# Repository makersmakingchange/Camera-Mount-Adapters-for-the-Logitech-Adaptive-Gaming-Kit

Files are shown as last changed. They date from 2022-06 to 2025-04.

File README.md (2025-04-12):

# Camera Mount Adapters for the Logitech Adaptive Gaming Kit

This Documentation covers information for both the full kit (12 adapters) and for a single adapter for one button.

The Camera Mount Adapters for Logitech Adaptive Gaming Kit are inexpensive, easy, and quick to build adapters for the four different Buttons from the [Logitech Adaptive Gaming Kit](<https://www.logitechg.com/en-ca/products/gamepads/adaptive-gaming-kit-accessories.943-000318.html/>). These adapters allow the buttons to be mounted on standard camera mounting equipment using the standard camera mount threads (¼”-20 UNC). These adapters were originally designed by [ATMakers](<http://atmakers.org/>) and more information on their switch mounts is available [here](<http://atmakers.org/2017/02/at-switch-adapters/>).

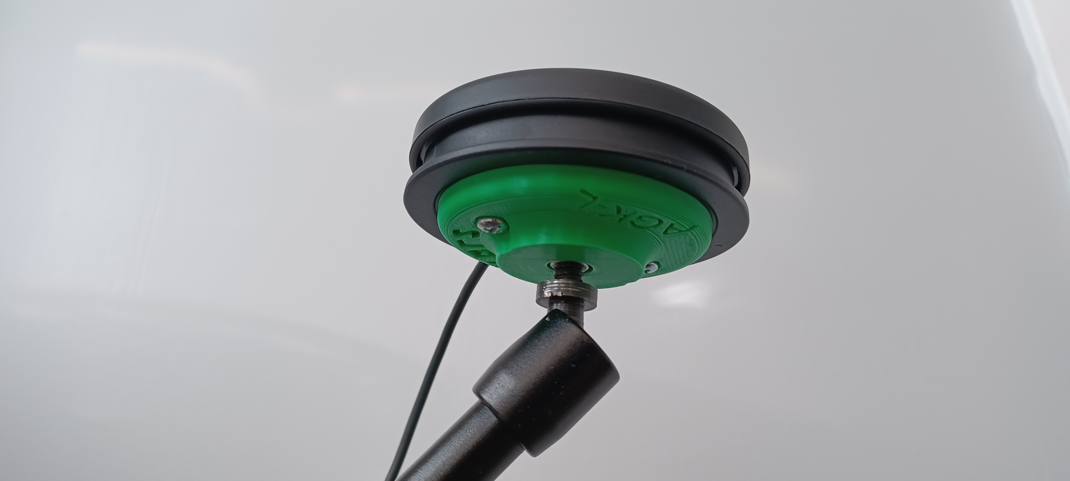
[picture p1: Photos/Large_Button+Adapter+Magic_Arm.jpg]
Camera Mount Adapters for the Logitech Adaptive Gaming Kit


## More info at
- [Makers Making Change Project Page](<https://makersmakingchange.com/project/camera-mount-adapters-for-the-logitech-adaptive-gaming-kit/>)

## Getting Started

### 1. Order the Off-The-Shelf Components

The [Bill of Materials](/Documentation/Camera_Adapter_Logitech_BOM_V1.1.csv) lists all of the parts and components required to build the Camera Mount Adapter for Logitech Adaptive Gaming Kit. Everything can either be 3D printed or bought at the local hardware store. 

### 2. Print the 3D Printable components

All of the files and individual print files can be in the [/Build_Files/](/Build_Files/) folder.

### 3. Assemble the device.

Reference the [Assembly Guide](/Documentation/Camera_Adapter_Logitech_Assembly_Guide_V1.1.pdf) for the tools and steps required to build the devices.
## Files
### Documentation
| Document             | Version | Link |
|----------------------|---------|------|
| Design Rationale     | 1.0     | [Camera_Adapter_Logitech_Design_Rationale](/Documentation/Camera_Adapter_Logitech_Design_Rationale_V1.1.pdf)     |
| Bill of Materials    | 1.0     | [Camera_Adapter_Logitech_Bill_of_Materials](/Documentation/Camera_Adapter_Logitech_BOM_V1.1.csv)     |
| Assembly Guide       | 1.0     | [Camera_Adapter_Logitech_Assembly_Guide](/Documentation/Camera_Adapter_Logitech_Assembly_Guide_V1.1.pdf)     |
| Maker Checklist      | 1.0     | [Camera_Adapter_Logitech_Maker_Checklist](/Documentation/Camera_Adapter_Logitech_Maker_Checklist_V1.1.pdf)     |
| User Guide           | 1.0     | [Camera_Adapter_Logitech_User_Guide](/Documentation/Camera_Adapter_Logitech_User_Guide_V1.1.pdf)    |
| Changelog            | 1.0     | [Camera_Adapter_Logitech_Changelog](/Documentation/Camera_Adapter_Logitech_Changelog_V1.1.pdf)     |
| Summary              | 1.0     | [Camera_Adapter_Logitech_Summary](/Documentation/Camera_Adapter_Logitech_Summary_V1.1.pdf)     |

### Design Files
[CAD Files](/Design_Files)

### Build Files
 - [3D Printing Files](/Build_Files)

## Attribution
[Original design](<https://www.thingiverse.com/thing:4128904>) created by [ATMakers](<http://atmakers.org/>) under the CC BY-SA 3.0 license.
Documentation, modified design, design files and build files created by Neil Squire / Makers Making Change under the CC BY-SA 4.0 license

## License
<br /><span xmlns:dct="http://purl.org/dc/terms/" property="dct:title">Camera Mount Adapters for the Logitech Adaptive Gaming Kit</span> by <a xmlns:cc="http://creativecommons.org/ns#" href="www.makersmakingchange.com" property="cc:attributionName" rel="cc:attributionURL">Neil Squire</a> is licensed under a <a rel="license" href="http://creativecommons.org/licenses/by-sa/4.0/">Creative Commons Attribution-ShareAlike 4.0 International License</a>.

---
<!-- ABOUT MMC START -->
## About Makers Making Change
[Makers Making Change Logo](https://www.makersmakingchange.com/)

Makers Making Change is a program of [Neil Squire](https://www.neilsquire.ca/), a Canadian non-profit that uses technology, knowledge, and passion to empower people with disabilities.

Makers Making Change leverages the capacity of community based Makers, Disability Professionals and Volunteers to develop and deliver affordable Open Source Assistive Technologies.

 - Website: [www.MakersMakingChange.com](https://www.makersmakingchange.com/)
 - GitHub: [makersmakingchange](https://github.com/makersmakingchange)
 - Bluesky: [@makersmakingchange.bsky.social](https://bsky.app/profile/makersmakingchange.bsky.social)
 - Instagram: [@makersmakingchange](https://www.instagram.com/makersmakingchange)
 - Facebook: [makersmakechange](https://www.facebook.com/makersmakechange)
 - LinkedIn: [Neil Squire Society](https://www.linkedin.com/company/neil-squire-society/)
 - Thingiverse: [makersmakingchange](https://www.thingiverse.com/makersmakingchange/about)
 - Printables: [MakersMakingChange](https://www.printables.com/@MakersMakingChange)

### Contact Us
For technical questions, to get involved, or to share your experience we encourage you to [visit our website](https://www.makersmakingchange.com/) or [contact us](https://www.makersmakingchange.com/s/contact).
<!-- ABOUT MMC END -->

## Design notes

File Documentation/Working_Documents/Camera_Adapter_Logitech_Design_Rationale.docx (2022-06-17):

# Introduction

The Logitech Adaptive Gaming Kit provides 4 different styles of assistive switches that can be set up in a personalized way for those with limited mobility and dexterity. The kit includes a hook and loop pad for arranging buttons on a flat surface, but this may be less than ideal for some users.

The Camera Mount Adapters for the Logitech Adaptive Gaming Kit are a set of adapters that enable a user to mount the buttons from the Logitech Adaptive Gaming Kit using a standard mounting system for camera equipment. There is a huge variety of inexpensive solutions to mount camera equipment, so this adapter greatly increases the customizability options for the buttons in the Logitech Adaptive Gaming Kit.

# Requirements

## Goals

G01 | To attach the assistive button from the Logitech Adaptive Gaming Kit to a standard ¼”-20 camera mounting system.

## Functional Requirements

F01 | The adapter must attach securely to the button.
F02 | The adapter must provide a female ¼"-20 UNC thread for mounting.

## Non-functional Requirement

NF01 | Any 3D printable components must be 3D printable using PLA.
NF02 | Must not deteriorate under daily use.

## Constraints

C01 | Single-build cost must be less than $10
C02 | Design must only include easy-to-source commercial components.

# Detailed Design

The Logitech Adaptive Gaming Kit consists of 4 types of buttons/triggers:

Size | Photo of Button | Photo of Camera Adapter
Large
Small
Trigger
Light Touch

ATMakers created a set of four adapters. A few modifications were incorporated to improve the designs as described below:

- Changed the length of the hole for the screws so that all buttons can be attached with an 8mm machine screw. This was especially important as the variable trigger button suffered immediate, albeit repairable damage, and the light touch button was not functional once a longer screw was used.
- The width of the countersink of the screw holes were widened from 5.5mm to 6.5mm in diameter to accommodate screws with wider heads.
- All the depths of the T-Nut inserts were different, some too deep or too shallow, so all were changed to 2.4 mm. (T-Nut flush with bottom with some margin)
- All the heights of the mounts were different, and all heights were changed to 9.5 mm. (T-Nut flush with top of mount).

Other important dimensions:

Small:

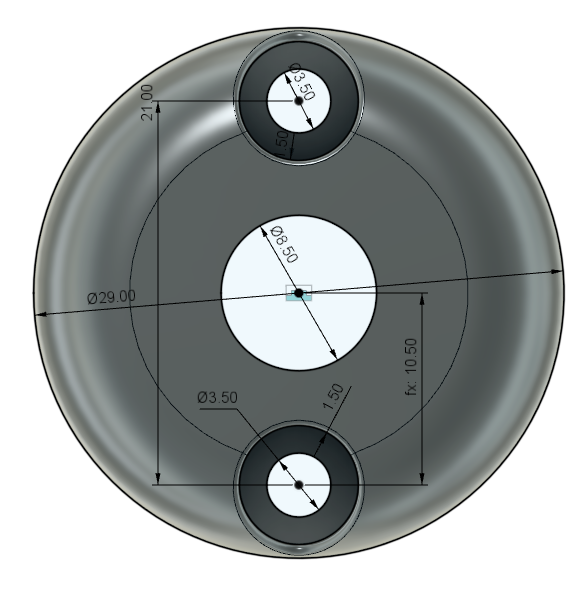
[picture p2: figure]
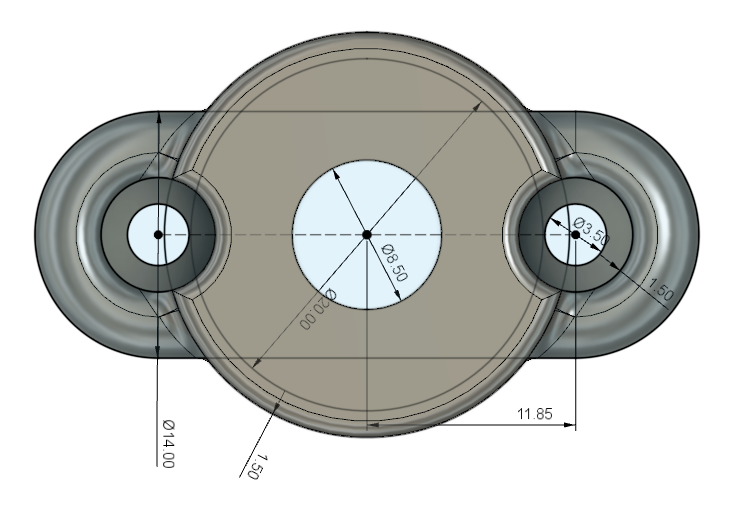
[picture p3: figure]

Light Touch:

Large:

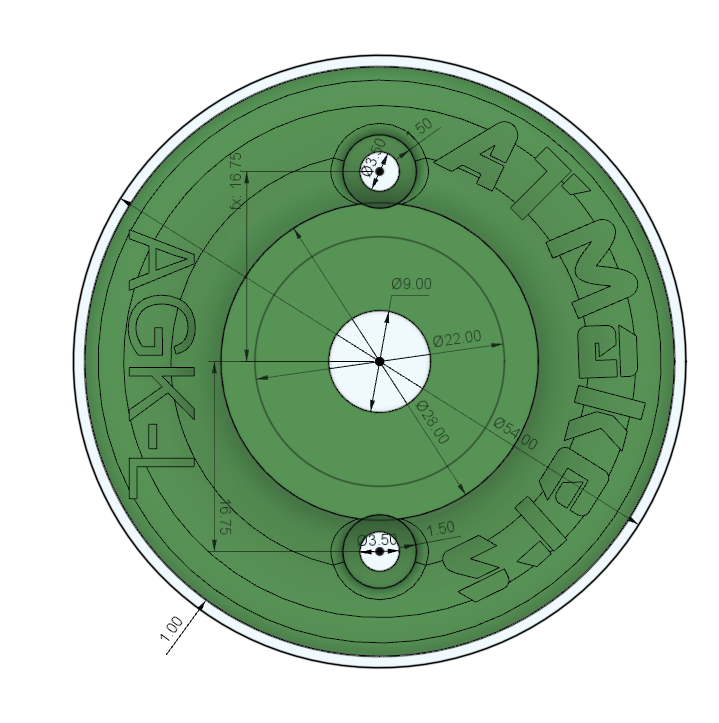
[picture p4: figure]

Variable Trigger:

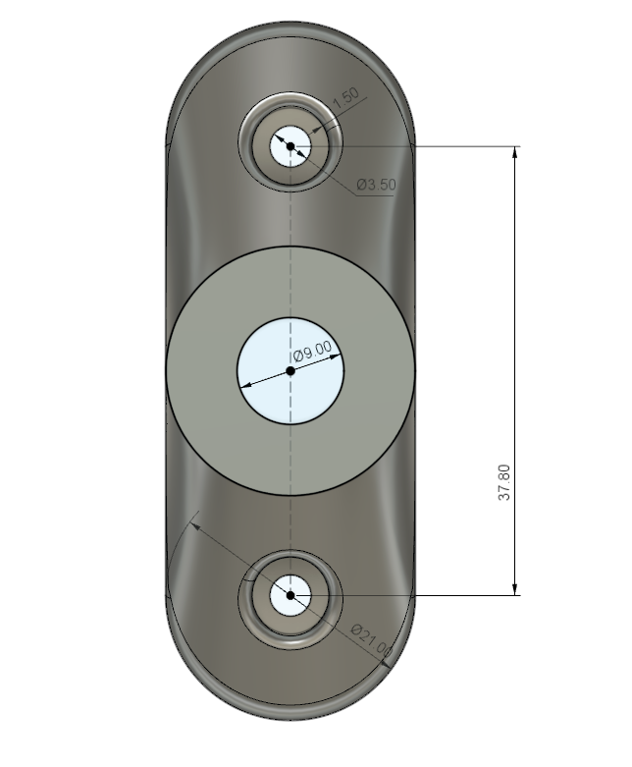
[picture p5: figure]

# Opportunities for Improvement

- Support can be difficult to remove from the 3D printed part, a design which doesn’t involve support may produce a better-quality device and take less time to build. For example, a sacrificial bridge could be used to reduce the support required to print the T-nut recess.

© 2022 by Neil Squire / Makers Making Change. This work is licensed under the CC BY SA 4.0 License: http://creativecommons.org/licenses/by-sa/4.0 Files available at https://makersmakingchange.com/camera-mount-adapters-for-the-logitech-adaptive-gaming-kit/ Page 1 of 1

V1.0 | June 2022 Camera Mount Adapters for the Logitech Adaptive Gaming Kit Design Rationale

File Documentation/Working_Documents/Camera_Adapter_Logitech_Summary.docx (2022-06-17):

# Title

Camera Mount Adapters for the Logitech Adaptive Gaming Kit.

## Subtitle

An adapter to fit the various buttons from the Logitech Adaptive Gaming Kit to camera mounts using ¼” – 20 threads.

## Device Specifications

Stage: Recently Added

Designer: AT Makers

Material Cost: $0 - $10

Disability Type: Mobility / Physical

Capabilities Needed: 3D Printing

Usage: Aids for Daily Living (ADL), Mobility, Computer Access

Difficulty: Beginner

Time to Complete: 1 – 4 hr

License: Attribution-ShareAlike 4.0 International

## Device Details

### Overview

The Camera Mount Adapters for Logitech Adaptive Gaming Kit are inexpensive, easy, and quick to build adapters for the four different Buttons from the Logitech Adaptive Gaming Kit (https://www.logitechg.com/en-us/products/gamepads/adaptive-gaming-kit-accessories.943-000318.html). These adapters allow the buttons to be mounted on standard camera mounting equipment using the standard camera mount threads (¼”-20 UNC). These adapters were originally designed by ATMakers (http://atmakers.org/) and more information on their switch mounts is available here (http://atmakers.org/2017/02/at-switch-adapters/).

### Usage

The Camera Mount Adapters for the Logitech Adaptive Gaming Kit are attached to the buttons by two screws. A ¼”-20 threaded T-Nut is attached to the adapter to provide reliable threads for camera mounting equipment such as tripods or mounting arms.

### Sizing

Size | Photo of Button | Photo of Camera Adapter

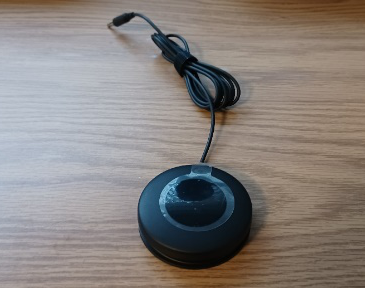
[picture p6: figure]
Logitech Large button on wood background.
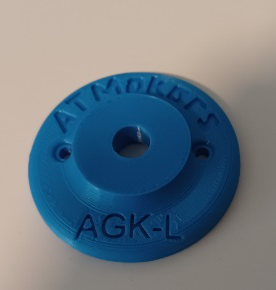
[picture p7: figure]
Camera mount adapter for Logitech Large Button on white background.

Large

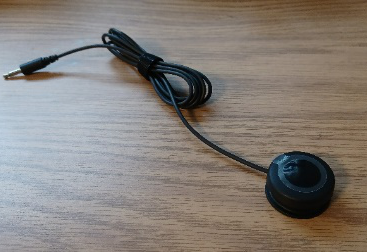
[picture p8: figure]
Logitech Small button on wood background.
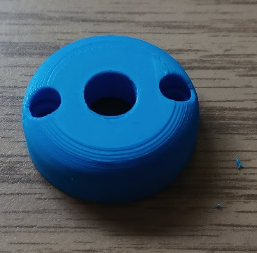
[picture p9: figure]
Camera mount adapter for Logitech Small Button on wood background.

Small

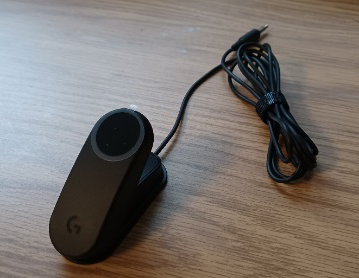
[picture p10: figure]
Logitech Trigger button on wood background.
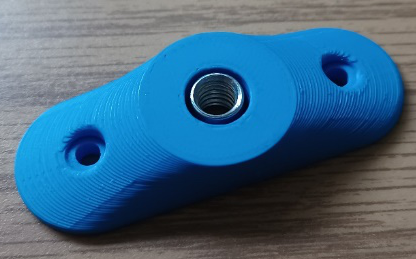
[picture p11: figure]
Camera mount adapter for Logitech Trigger Button on wood background.

Trigger

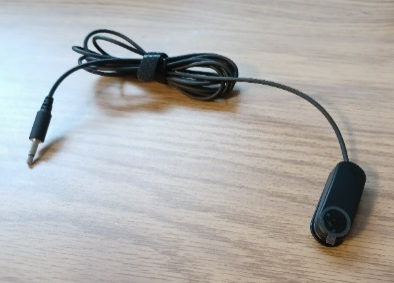
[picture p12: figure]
Logitech Light Touch button on wood background.
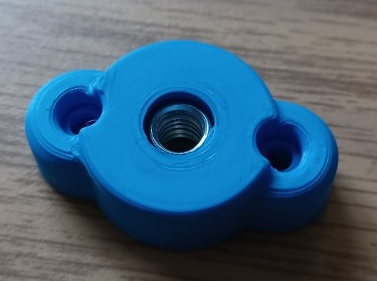
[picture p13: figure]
Camera mount adapter for Logitech Large Button on wood background.

Light Touch

## Compatibility

This device is compatible with the appropriate buttons from the Logitech Adaptive Gaming Kit only.
Logitech G Adaptive Gaming Kit for the Xbox - Canada (https://www.logitechg.com/en-ca/products/gamepads/adaptive-gaming-kit-accessories.943-000318.html)

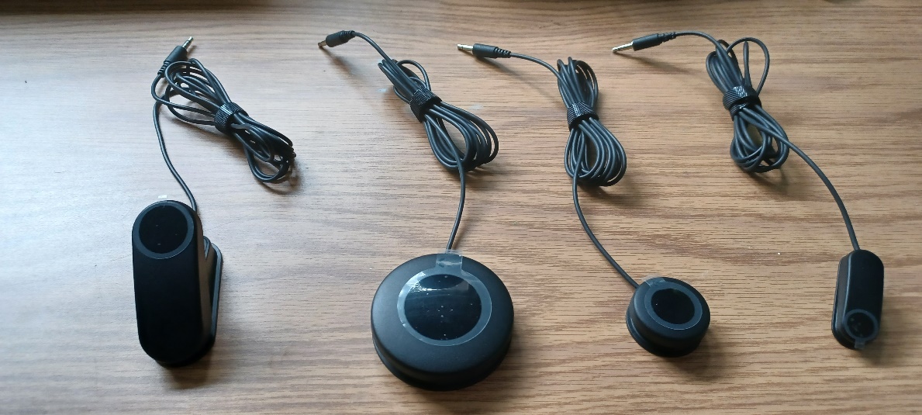
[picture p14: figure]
All Logitech buttons from the Logitech Adaptive Gaming Kit on a wood background.

### Camera Mounting Options:

Some possible mounting options using these camera mount adapters are tripods, flexible “gooseneck” mounts or a magic arm as shown below:

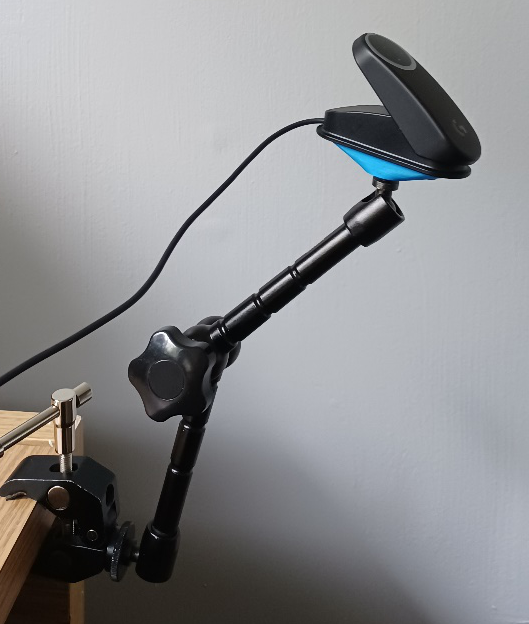
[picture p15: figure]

### Cost

The total cost of this device includes the cost of the PLA filament used to print the device, the T-Nut used to provide threads, and the two screws used to attach the device to the appropriate Logitech Button.

The total cost of one mount comes to approximately $2.26 (price calculated using the largest and most expensive mount).

The total cost of the full kit (12 mounts) comes to approximately $26.15.

A ¼” washer and a ¼” – 20 screw (at least ½” length) are temporarily needed to install the T-Nut. If needed to purchase, this will increase the cost of the device to approximately $2.

A more complete Bill of Materials is provided in the BOM spreadsheet in the linked GitHub repository.

### Build Instructions

This device consists of a single 3D-Printed part, two screws and one T-Nut. The necessary files and instructions for 3D printing as well as the assembly guide are in the linked GitHub Repository.

#### Skills Required

- 3D Printing

#### Time Required

For single mount:

- 3D printing ~1.5 hours
- Assembly ~10 minutes

For full kit:

- 3D printing ~11.57 hours
- Assembly ~30 minutes

#### Tools

- 3D Printer
- Screwdriver
- ¼”-20 machine screw (at least ½” length) and washer for assembly.

#### Components

- 3D-Printed housing.
- ¼”-20 Barbed T-Nut 5/16” barrel length.
- 2x M3 x 8mm machine screws.

#### 3D Printing

Refer to the 3D Printing Guide available in the Linked GitHub Repository.

### Attribution

Original design (https://www.thingiverse.com/thing:4128904) created by ATMakers (http://atmakers.org/) under the CC BY-SA 3.0 license.

Documentation, modified design, design files and build files created by Neil Squire / Makers Making Change under the CC BY-SA 4.0 license

© 2022 by Neil Squire / Makers Making Change. This work is licensed under the CC BY SA 4.0 License: http://creativecommons.org/licenses/by-sa/4.0 Files available at https://makersmakingchange.com/camera-mount-adapters-for-the-logitech-adaptive-gaming-kit/ Page 1 of 2

V1.0 | June 2022 Camera Mount Adapters for the Logitech Adaptive Gaming Kit Summary

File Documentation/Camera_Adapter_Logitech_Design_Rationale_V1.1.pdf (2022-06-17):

V1.0 | June 2022

## Camera Mount Adapters for the Logitech Adaptive Gaming Kit

## DESIGN RATIONALE

© 2022 by Neil Squire / Makers Making Change. This work is licensed under the CC BY SA 4.0 License: http://creativecommons.org/licenses/by-sa/4.0
Files available at https://makersmakingchange.com/camera-mount-adapters-for-the-logitech-adaptive-gaming-kit/ (https://makersmakingchange.com/project/camera-mount-adapter-for-logitech-large-button/)

### Introduction

The Logitech Adaptive Gaming Kit provides 4 different styles of assistive switches that can be set up in a personalized way for those with limited mobility and dexterity. The kit includes a hook and loop pad for arranging buttons on a flat surface, but this may be less than ideal for some users.

The Camera Mount Adapters for the Logitech Adaptive Gaming Kit are a set of adapters that enable a user to mount the buttons from the Logitech Adaptive Gaming Kit using a standard mounting system for camera equipment. There is a huge variety of inexpensive solutions to mount camera equipment, so this adapter greatly increases the customizability options for the buttons in the Logitech Adaptive Gaming Kit.

### Requirements

### Goals

G01 To attach the assistive button from the Logitech Adaptive Gaming Kit to a standard ¼”-20 camera mounting system.

### Functional Requirements

F01 | The adapter must attach securely to the button.
F02 | The adapter must provide a female ¼"-20 UNC thread for mounting.

### Non-functional Requirement

NF01 | Any 3D printable components must be 3D printable using PLA.
NF02 | Must not deteriorate under daily use.

### Constraints

C01 | Single-build cost must be less than $10
C02 | Design must only include easy-to-source commercial components.

### Detailed Design

The Logitech Adaptive Gaming Kit consists of 4 types of buttons/triggers:

Size | Photo of Button | Photo of Camera Adapter

## Logitech Adaptive Gaming Kit

## DESIGN RATIONALE

© 2022 by Neil Squire / Makers Making Change.

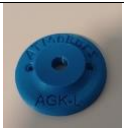
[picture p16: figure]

Large

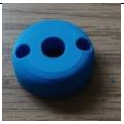
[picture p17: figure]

Small

Trigger

Light Touch

ATMakers created a set of four adapters. A few modifications were incorporated to improve the designs as described below:

- Changed the length of the hole for the screws so that all buttons can be attached with an 8mm machine screw. This was especially important as the variable trigger button suffered immediate, albeit repairable damage, and the light touch button was not functional once a longer screw was used.

## Logitech Adaptive Gaming Kit

## DESIGN RATIONALE

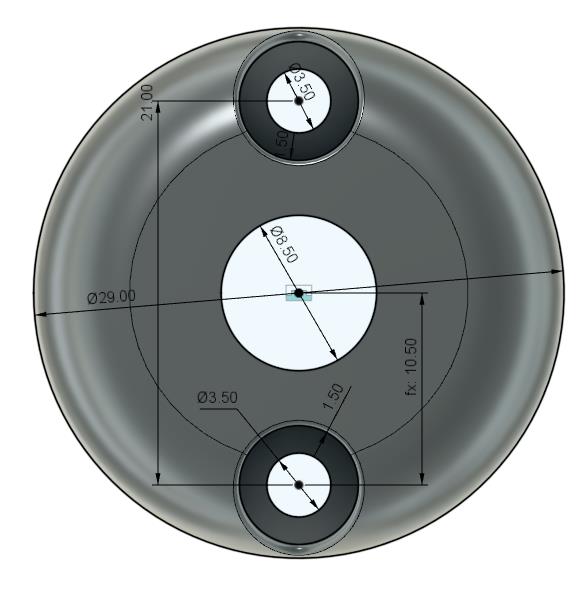
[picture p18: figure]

© 2022 by Neil Squire / Makers Making Change.

- The width of the countersink of the screw holes were widened from 5.5mm to 6.5mm in diameter to accommodate screws with wider heads.
- All the depths of the T-Nut inserts were different, some too deep or too shallow, so all were changed to 2.4 mm. (T-Nut flush with bottom with some margin)
- All the heights of the mounts were different, and all heights were changed to 9.5 mm. (T-Nut flush with top of mount).

Other important dimensions:

Small:

## Logitech Adaptive Gaming Kit

## DESIGN RATIONALE

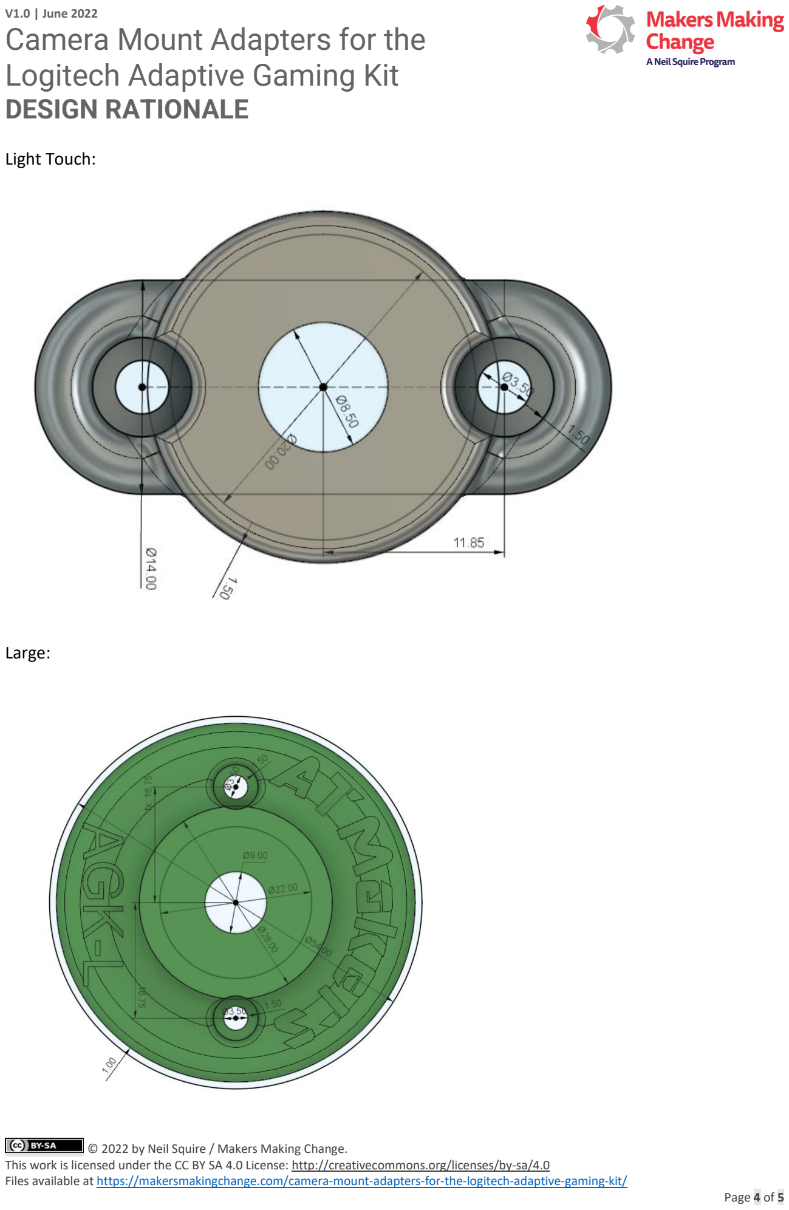
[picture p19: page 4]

© 2022 by Neil Squire / Makers Making Change.

Light Touch:

Large:

## Logitech Adaptive Gaming Kit

## DESIGN RATIONALE

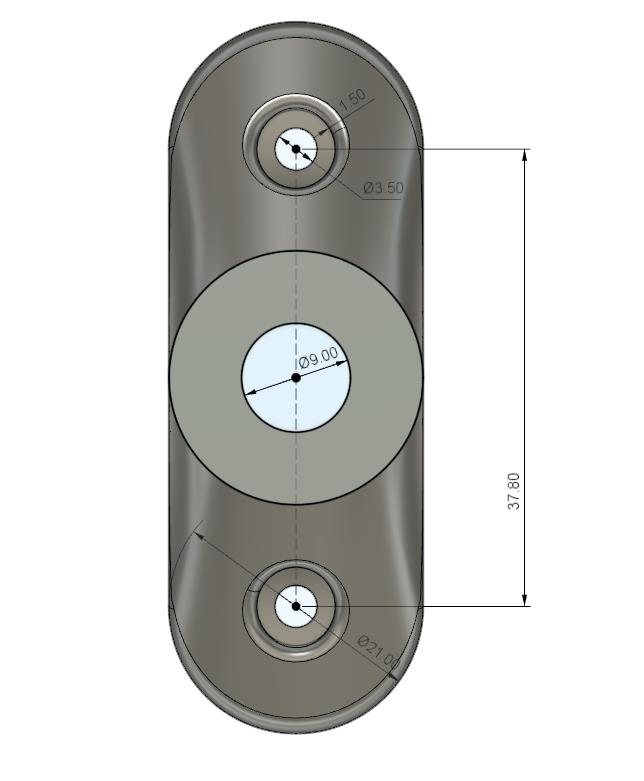
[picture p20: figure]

© 2022 by Neil Squire / Makers Making Change.

Variable Trigger:

### Opportunities for Improvement

- Support can be difficult to remove from the 3D printed part, a design which doesn’t involve support may produce a better-quality device and take less time to build. For example, a sacrificial bridge could be used to reduce the support required to print the T-nut recess.

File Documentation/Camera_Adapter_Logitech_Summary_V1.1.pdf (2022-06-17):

V1.0 | June 2022

## Camera Mount Adapters for the Logitech Adaptive Gaming Kit

## SUMMARY

© 2022 by Neil Squire / Makers Making Change. This work is licensed under the CC BY SA 4.0 License: http://creativecommons.org/licenses/by-sa/4.0
Files available at https://makersmakingchange.com/camera-mount-adapters-for-the-logitech-adaptive-gaming-kit/ (https://makersmakingchange.com/project/camera-mount-adapter-for-logitech-large-button/) | Page 1 of 5

### Title

Camera Mount Adapters for the Logitech Adaptive Gaming Kit.

### Subtitle

An adapter to fit the various buttons from the Logitech Adaptive Gaming Kit to camera mounts using ¼” – 20 threads.

### Device Specifications

Stage: Recently Added

Designer: AT Makers

Material Cost: $0 - $10

Disability Type: Mobility / Physical

Capabilities Needed: 3D Printing

Usage: Aids for Daily Living (ADL), Mobility, Computer Access

Difficulty: Beginner

Time to Complete: 1 – 4 hr

License: Attribution-ShareAlike 4.0 International

### Device Details

Overview
The Camera Mount Adapters for Logitech Adaptive Gaming Kit are inexpensive, easy, and quick to build adapters for the four different Buttons from the Logitech Adaptive Gaming Kit. (https://www.logitechg.com/en-us/products/gamepads/adaptive-gaming-kit-accessories.943-000318.html) These adapters allow the buttons to be mounted on standard camera mounting equipment using the standard camera mount threads (¼”-20 UNC). These adapters were originally designed by ATMakers (http://atmakers.org/) and more information on their switch mounts is available here. (http://atmakers.org/2017/02/at-switch-adapters/)

Usage
The Camera Mount Adapters for the Logitech Adaptive Gaming Kit are attached to the buttons by two screws. A ¼”-20 threaded T-Nut is attached to the adapter to provide reliable threads for camera mounting equipment such as tripods or mounting arms.

## Logitech Adaptive Gaming Kit

## SUMMARY

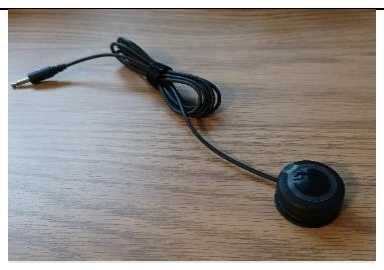
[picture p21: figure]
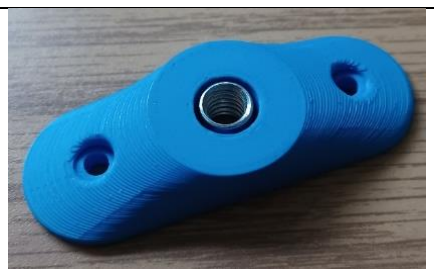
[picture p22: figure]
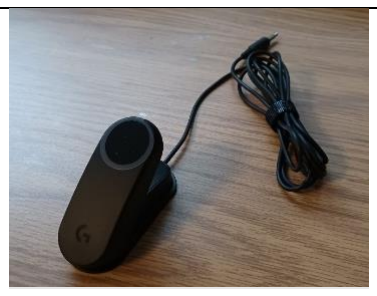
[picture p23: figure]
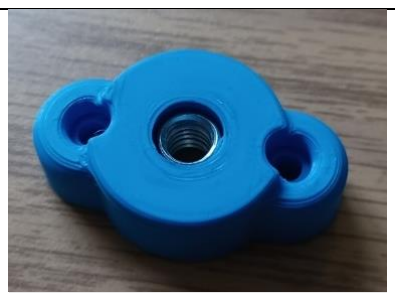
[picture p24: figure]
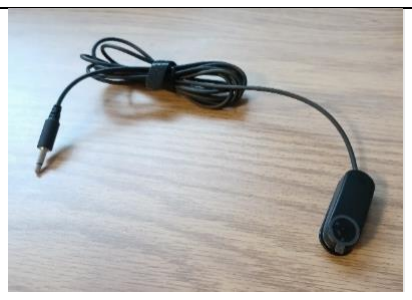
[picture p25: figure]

Files available at https://makersmakingchange.com/camera-mount-adapters-for-the-logitech-adaptive-gaming-kit/ (https://makersmakingchange.com/project/camera-mount-adapter-for-logitech-large-button/) | Page 2 of 5


Sizing


Size | Photo of Button | Photo of Camera Adapter

Large

Small

Trigger

Light Touch

## Logitech Adaptive Gaming Kit

## SUMMARY


Files available at https://makersmakingchange.com/camera-mount-adapters-for-the-logitech-adaptive-gaming-kit/ (https://makersmakingchange.com/project/camera-mount-adapter-for-logitech-large-button/) | Page 3 of 5

### Compatibility

This device is compatible with the appropriate buttons from the Logitech Adaptive Gaming Kit only. Logitech G Adaptive Gaming Kit for the Xbox - Canada (https://www.logitechg.com/en-ca/products/gamepads/adaptive-gaming-kit-accessories.943-000318.html)

Camera Mounting Options:

Some possible mounting options using these camera mount adapters are tripods, flexible “gooseneck” mounts or a magic arm as shown below:

Cost
The total cost of this device includes the cost of the PLA filament used to print the device, the T-Nut used to provide threads, and the two screws used to attach the device to the appropriate Logitech Button.

## Logitech Adaptive Gaming Kit

## SUMMARY

Files available at https://makersmakingchange.com/camera-mount-adapters-for-the-logitech-adaptive-gaming-kit/ (https://makersmakingchange.com/project/camera-mount-adapter-for-logitech-large-button/) | Page 4 of 5

The total cost of one mount comes to approximately $2.26 (price calculated using the largest and most expensive mount).

The total cost of the full kit (12 mounts) comes to approximately $26.15.

A ¼” washer and a ¼” – 20 screw (at least ½” length) are temporarily needed to install the T-Nut. If needed to purchase, this will increase the cost of the device to approximately $2.

A more complete Bill of Materials is provided in the BOM spreadsheet in the linked GitHub repository.

Build Instructions
This device consists of a single 3D-Printed part, two screws and one T-Nut. The necessary files and instructions for 3D printing as well as the assembly guide are in the linked GitHub Repository.

Skills Required
- 3D Printing

Time Required
For single mount:
- 3D printing ~1.5 hours
- Assembly ~10 minutes

For full kit:

- 3D printing ~11.57 hours
- Assembly ~30 minutes

Tools
- 3D Printer
- Screwdriver
- ¼”-20 machine screw (at least ½” length) and washer for assembly.

Components
- 3D-Printed housing.
- ¼”-20 Barbed T-Nut 5/16” barrel length.
- 2x M3 x 8mm machine screws.

3D Printing
Refer to the 3D Printing Guide available in the Linked GitHub Repository.

## Logitech Adaptive Gaming Kit

## SUMMARY

Files available at https://makersmakingchange.com/camera-mount-adapters-for-the-logitech-adaptive-gaming-kit/ (https://makersmakingchange.com/project/camera-mount-adapter-for-logitech-large-button/) | Page 5 of 5

Attribution
Original design (https://www.thingiverse.com/thing:4128904) created by ATMakers (http://atmakers.org/) under the CC BY-SA 3.0 license.

Documentation, modified design, design files and build files created by Neil Squire / Makers Making Change under the CC BY-SA 4.0 license

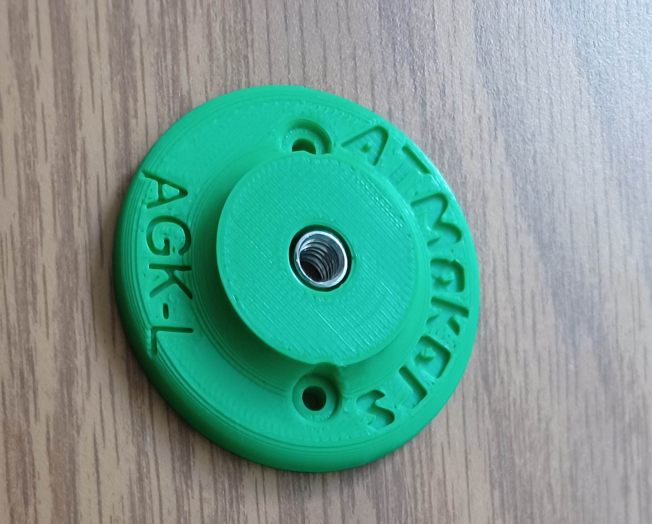
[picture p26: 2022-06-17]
Photos/Large_Adapter.jpg

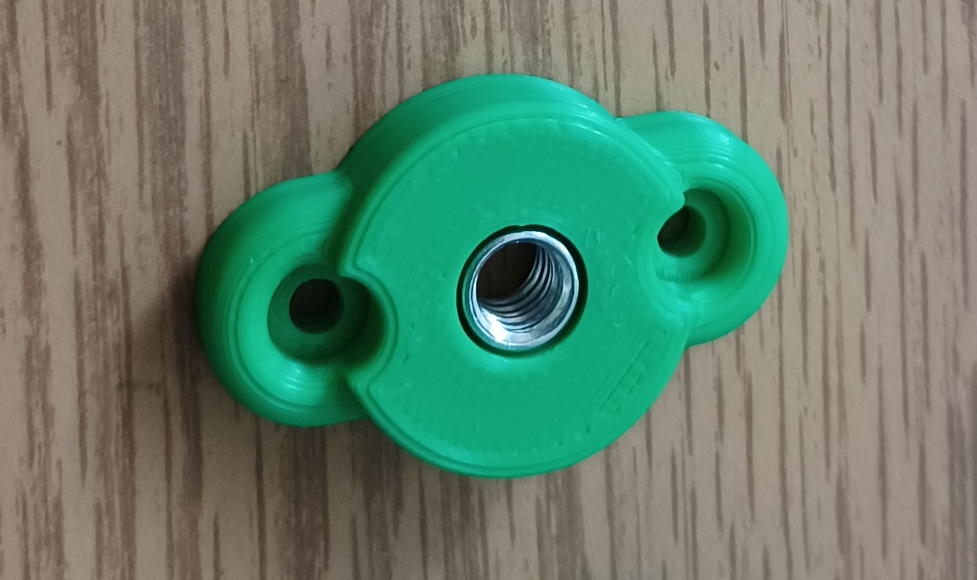
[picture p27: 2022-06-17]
Photos/Light_Touch_Adapter.jpg

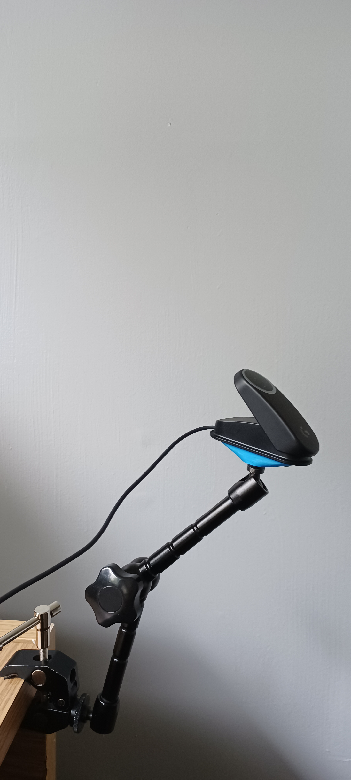
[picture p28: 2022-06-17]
Photos/Trigger_Adapter+Button+Magic_Arm.jpg

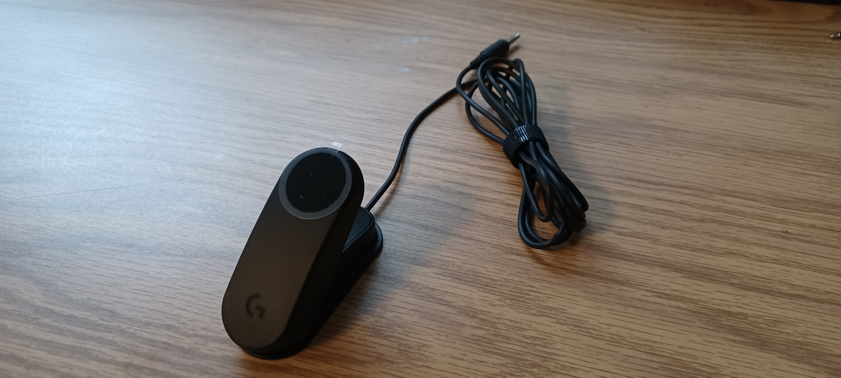
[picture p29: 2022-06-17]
Photos/Trigger_Button.jpg

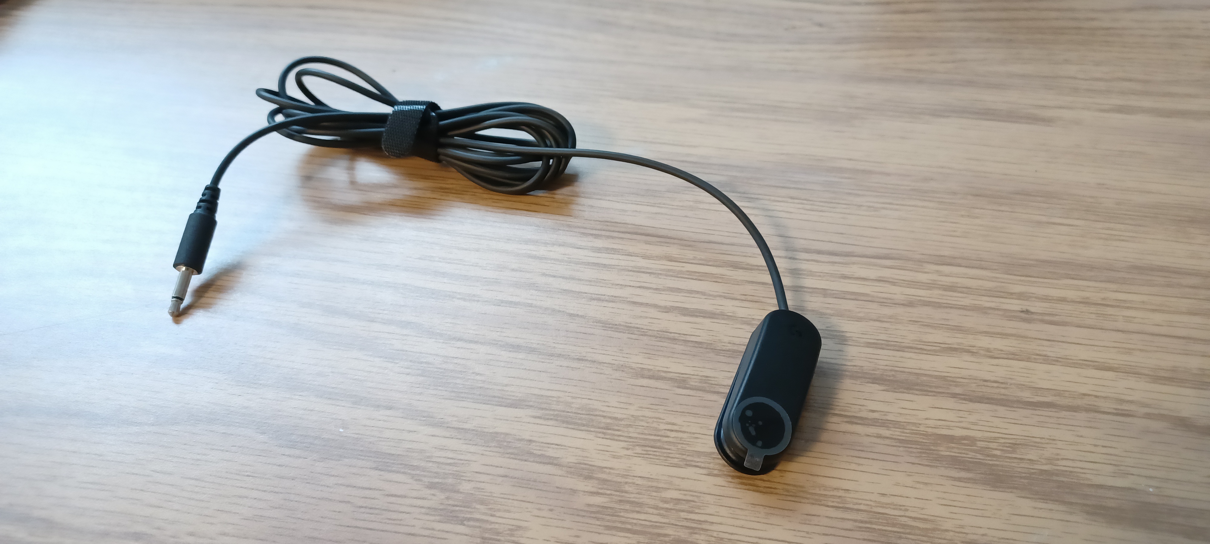
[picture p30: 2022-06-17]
Photos/Light_Touch_Button.jpg

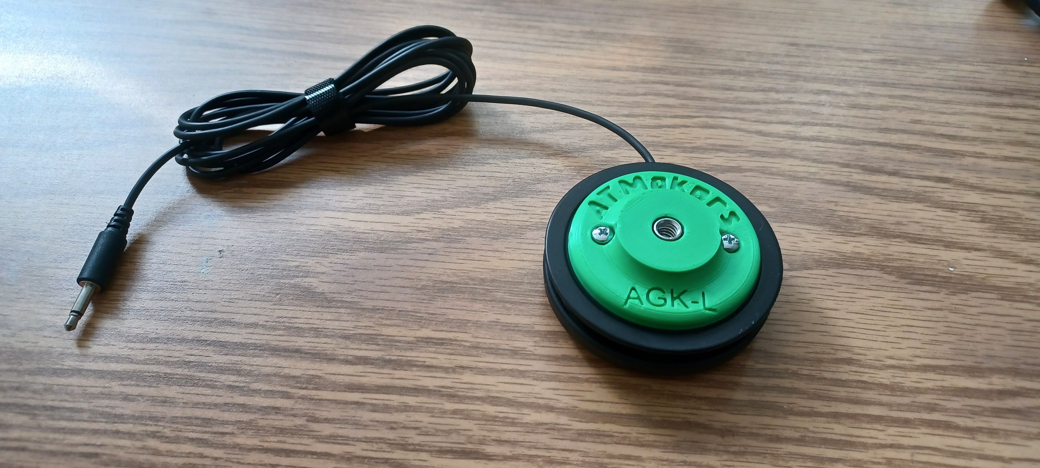
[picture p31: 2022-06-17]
Photos/Large_Adapter+Button.jpg

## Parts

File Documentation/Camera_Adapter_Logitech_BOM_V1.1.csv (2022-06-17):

Camera Mount Adapters for the Logitech Adaptive Gaming Kit |  | Total Cost | Total Print time (hr) | Total filament (g)
Version: V1.0 | Date Created: 4/20/2021 | $2.26 | 1.18 | 10
For One Mount (Single Button)
Commercial Parts:
Part type (Electrical. Mechanical, Sanitization, ect) | Part Name | Quantity Needed | Pkg Quantity | Price per package | Price per Unit | Price for qty needed | Link
Mechanical | 1/4" - 20 Barbed T-Nut 5/16" barrel length. (Important Note: the mount for the small Logitech buttons requires a T-Nut with four prongs, not three. The other mounts can use both three-pronged and 4-pronged T-Nuts.) | 1 | 1 | $0.69 | $0.69 | $0.69 | https://www.canadiantire.ca/en/pdp/hillman-tee-nuts-zinc-1612084p.1612085.html
Mechanical | M3 x 8mm Machine Screws | 2 | 5 | $3.29 | $0.66 | $1.32 | https://www.canadiantire.ca/en/pdp/hillman-metric-pan-head-phillips-machine-screws-1612644p.1612656.html?rrec=true
3D Printed Parts ESTIMATED PRICING USING 1KG ROLL COST: | $25.00
Part | Description | Quantity Needed | TOTAL Mass (g) | Estimated Price | Print Time (Min) | Link
xxxxx.stl (Where xxxxx corresponds to the size of the button and the respective adapter.) | The adapter for the 1/4"-20 threads which can be attached to a button from the Logitech Adaptive Gaming Kit. | 1 | 10 | $0.25 | 71 | Camera-Mount-Adapters-for-the-Logitech-Adaptive-Gaming-Kit/Build_Files at main · makersmakingchange/Camera-Mount-Adapters-for-the-Logitech-Adaptive-Gaming-Kit (github.com)
 |  |  | Total Print Cost: | $0.25
Tools for Assembly
1/4" washer - for installing T-Nut
1/4"-20 Screw - for installing T-Nut
Screwdriver - to fit the head socket of the M3 and 1/4"-20 screws.
 |  | Total Cost | Total Print time (hr) | Total filament (g)
For All Mounts (12 total buttons) |  | $26.15 | 11.57 | 83
Commercial Parts:
Part type (Electrical. Mechanical, Sanitization, ect) | Part Name | Quantity Needed | Pkg Quantity | Price per package | Price per Unit | Price for qty needed | Link
Mechanical | 1/4" - 20 Barbed T-Nut 5/16" barrel length. (Important Note: the mount for the small Logitech buttons requires a T-Nut with four prongs, not three. The other mounts can use both three-pronged and 4-pronged T-Nuts.) | 12 | 1 | $0.69 | $0.69 | $8.28 | https://www.canadiantire.ca/en/pdp/hillman-tee-nuts-zinc-1612084p.1612085.html
Mechanical | M3 x 8mm Machine Screws | 24 | 5 | $3.29 | $0.66 | $15.79 | https://www.canadiantire.ca/en/pdp/hillman-metric-pan-head-phillips-machine-screws-1612644p.1612656.html?rrec=true
3D Printed Parts ESTIMATED PRICING USING 1KG ROLL COST: | $25.00
Part | Description | Quantity Needed | TOTAL Mass (g) | Estimated Price | Print Time (Min) | Link
Large.stl | The adapter for the 1/4"-20 threads which can be attached to the Logitech Large Button from the Adaptive Gaming Kit. | 3 | 33 | $0.83 | 219 | Camera-Mount-Adapters-for-the-Logitech-Adaptive-Gaming-Kit/Build_Files at main · makersmakingchange/Camera-Mount-Adapters-for-the-Logitech-Adaptive-Gaming-Kit (github.com)
Small.stl | The adapter for the 1/4"-20 threads which can be attached to the Logitech small Button from the Adaptive Gaming Kit. | 3 | 12 | $0.30 | 205
Trigger.stl | The adapter for the 1/4"-20 threads which can be attached to the Logitech Variable Trigger Button from the Adaptive Gaming Kit. | 2 | 18 | $0.45 | 94
Light_Touch.stl | The adapter for the 1/4"-20 threads which can be attached to the Logitech Light Touch Button from the Adaptive Gaming Kit. | 4 | 20 | $0.50 | 176
 |  |  | Total Print Cost: | $2.08
Tools for Assembly
1/4" washer - for installing T-Nut
1/4"-20 Screw - for installing T-Nut
Screwdriver - to fit the head socket of the M3 and 1/4"-20 screws.

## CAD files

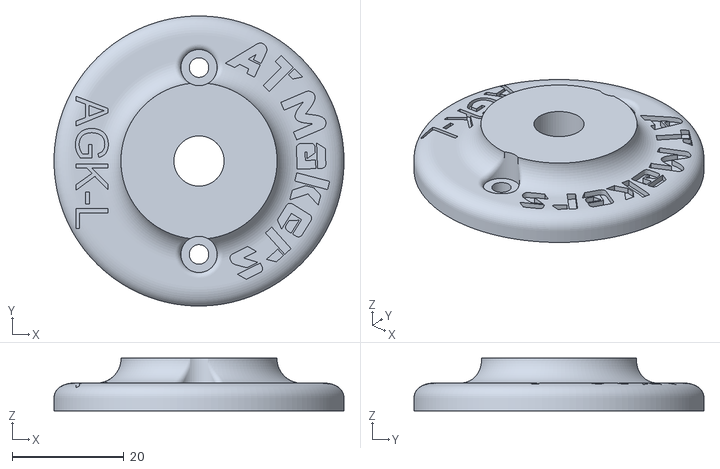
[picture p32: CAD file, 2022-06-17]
Build_Files/Logitech_Large.stl
52.0 x 52.0 x 9.50

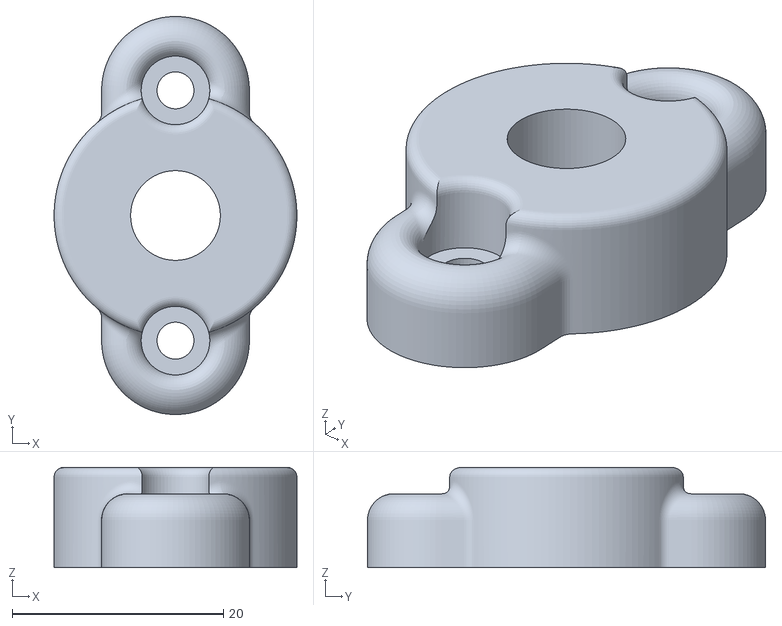
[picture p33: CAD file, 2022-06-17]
Build_Files/Logitech_Light_Touch.stl
23.0 x 37.7 x 9.50

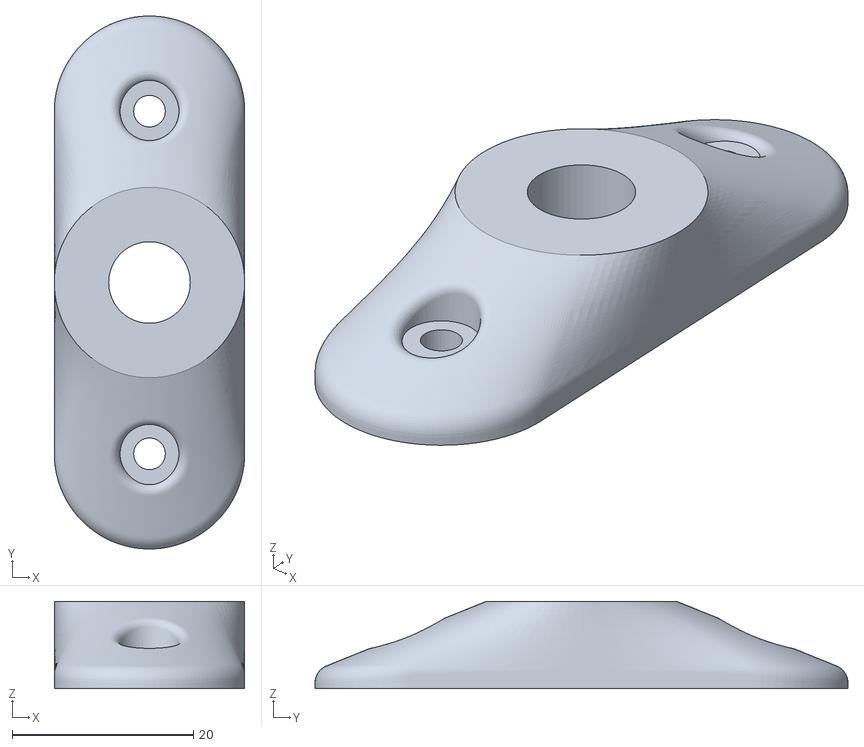
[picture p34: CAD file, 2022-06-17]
Build_Files/Logitech_Trigger.stl
21.0 x 58.8 x 9.63

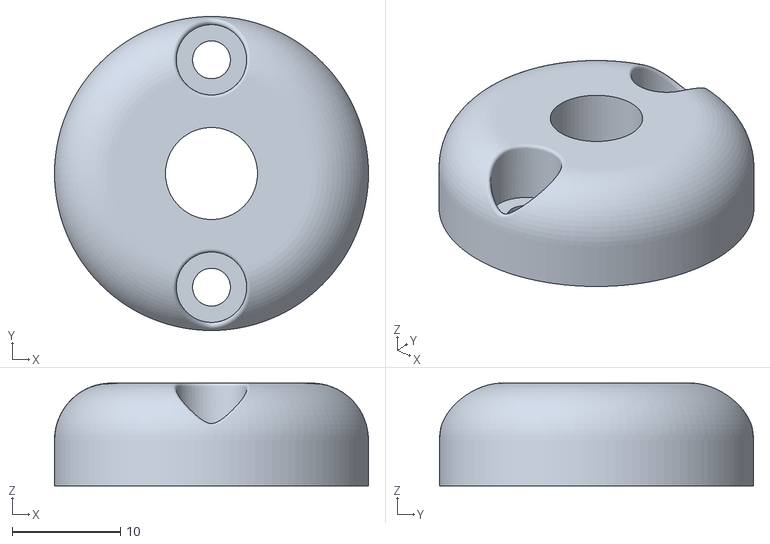
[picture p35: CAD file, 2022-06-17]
Build_Files/Logitech_Small.stl
29.0 x 29.0 x 9.50

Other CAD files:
Design_Files/Logitech_Large v6.f3d
Design_Files/Logitech_Light_Touch v5.f3d
Design_Files/Logitech_Small v10.f3d
Design_Files/Logitech_Small v12.f3d
Design_Files/Logitech_Trigger v6.f3d

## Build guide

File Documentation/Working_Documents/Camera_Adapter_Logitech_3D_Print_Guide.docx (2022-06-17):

# 3D Printing Summary

Metrics | Entire Set
Total Print Time (min) | 9:54
Total Number of Components | 12
Typical Total Mass (g) | 10
Typical Number of Print Setups | 4

# 3D Printing Settings

Print File Name | Qty | Individual Print Time (hr:min) | Total Print Time (hr:min) | Individual Mass (g) | Total Mass (g) | Infill (%) | Support | Layer Height/ Nozzle Diameter(mm) | Notes (orientation, special settings, etc)
Large.stl | 3 | 1:13 | 3:39 | 11 | 33 | 20 | Support Required | 0.2/0.4 | - Needs Support Touching Build plate only - 2 perimeters minimum
Trigger.stl | 2 | 0:47 | 1:34 | 6 | 18 | 20 | Support Required | 0.2/0.4 | - Needs Support Touching Build plate only - 2 perimeters minimum
Small.stl | 3 | 0:35 | 1:45 | 4 | 12 | 20 | Support Required | 0.2/0.4 | - Needs Support Touching Build plate only - 2 perimeters minimum
Light_Touch.stl | 4 | 0:44 | 2:56 | 5 | 20 | 20 | Support Required | 0.2/0.4 | - Needs Support Touching Build plate only - 2 perimeters minimum

# Customization Options

- Can be printed in any colour.

# Post-Processing

- Remove supports ensuring holes for barbs in T-nuts are uncovered.
- Follow Assembly guide for complete instructions on mounting the Logitech Large Button.

# Examples of Quality Prints

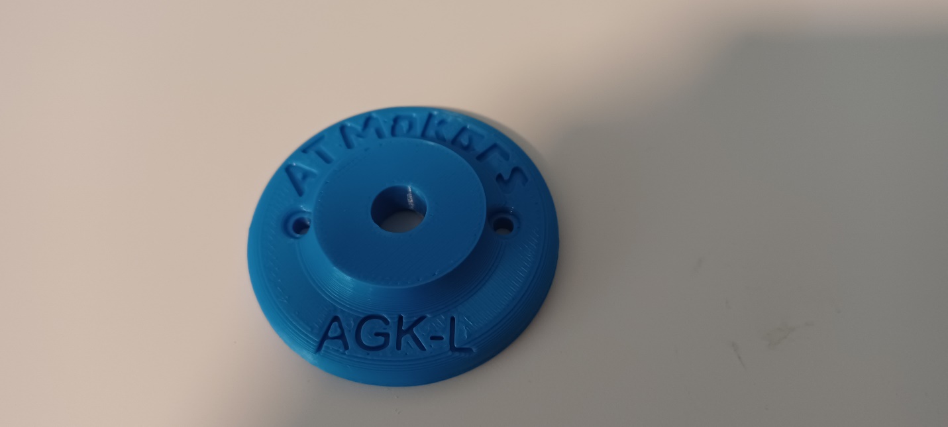
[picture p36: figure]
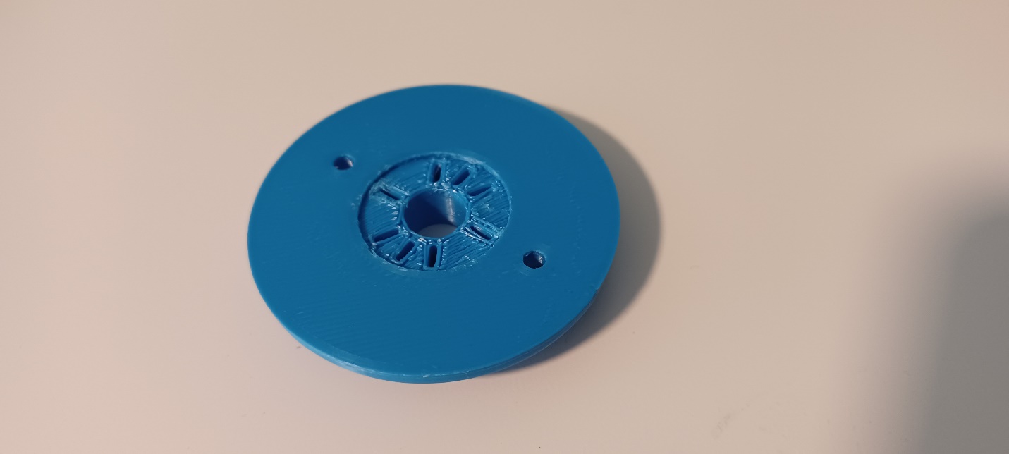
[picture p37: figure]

© 2022 by Neil Squire / Makers Making Change This work is licensed under the CC BY SA 4.0 License: http://creativecommons.org/licenses/by-sa/4.0 Files available at https://makersmakingchange.com/camera-mount-adapters-for-the-logitech-adaptive-gaming-kit/ Page 1 of 2

V1.0 | June 2022 Camera Mount Adapters for the Logitech Adaptive Gaming Kit 3D Printing Guide

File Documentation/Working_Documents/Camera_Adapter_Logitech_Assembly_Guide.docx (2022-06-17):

# Required Components

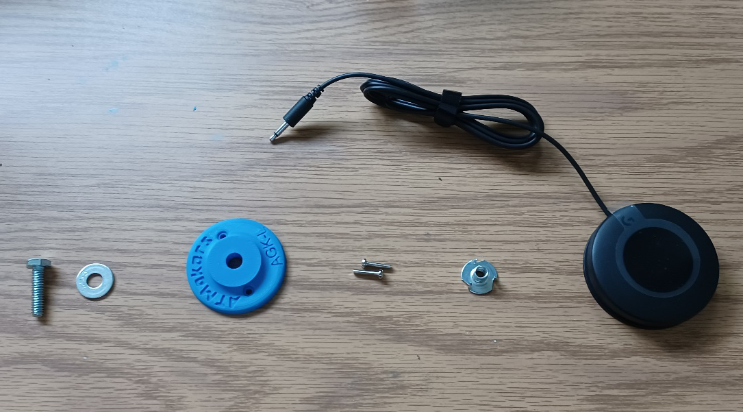
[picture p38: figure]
Image showing all parts needed to assemble Camera Adapter for Logitech Adaptive Gaming Kit, and assigning a number.

6 5 4 1 2 3 | BOM 1. Main Housing 2. 1/4”-20 Machine Screw – Temporarily used for installing T-Nut. 3. ¼” Washer – Temporarily used for installing T-Nut. 4. 2x M3 x 8mm Machine Screws 5. Barbed ¼” -20 T-Nut 5.16” Barrel length. 6. Logitech Adaptive Gaming Kit Button (Example shown is the Large Button)

# Required Tools

- Screwdriver compatible with the M3 machine screws and the ¼” – 20 machine screw.

# Required Personal Protective Equipment (PPE)

- None

# Assembly Instructions

## Step 1

Place the 3D-Printed Housing upside down on a table so that the text is facing downwards. Insert the T-Nut as far as possible into the hole by hand.

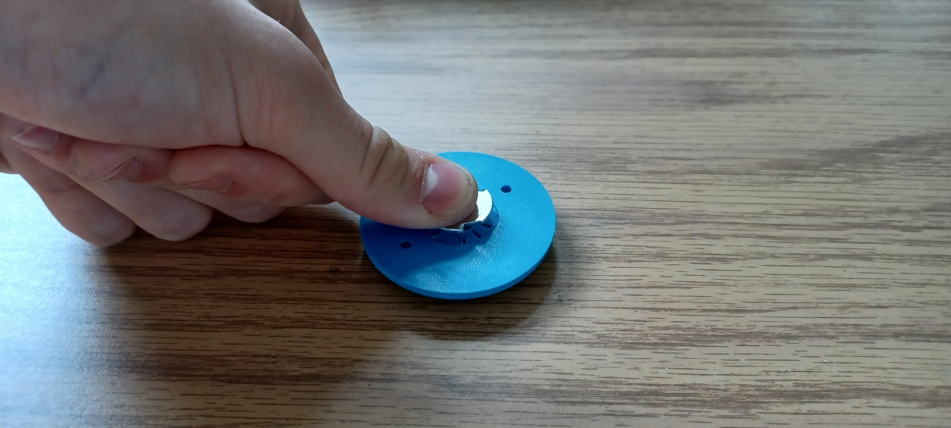
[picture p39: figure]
Hand pushes T-Nut as far as possible into the main housing of the adapter.

## Step 2

Flip the device so that the text is facing up and the T-Nut is sitting on the table. Put the ¼” washer on the ¼”-20 screw, then place the screw inside the hole from the top so that the washer prevents it from falling through.

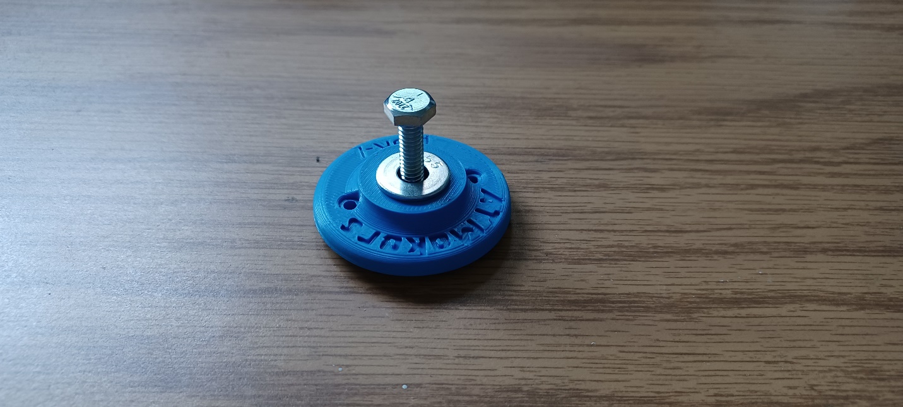
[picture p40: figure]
Screw and Washer are placed on the main housing of the adapter in preparation for installing the T-Nut.

## Step 3

Tighten the screw as far as possible. The T-Nut should be secured in place at the bottom of the device.

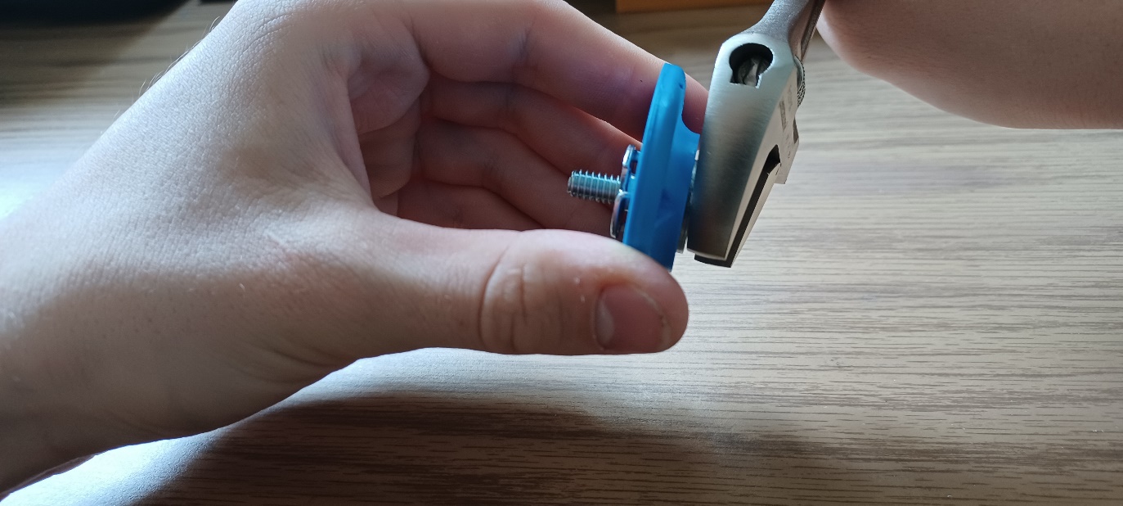
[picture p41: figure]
A wrench is used to tighten the 1/4" inch screw as far as possible into the T-Nut, pressing the T-Nut into the housing.

Step 5

Line up the screw threads with the holes in the bottom of the Large Button from the Logitech Adaptive Gaming Kit. Tighten these screws to attach the Camera Mount Adapter.

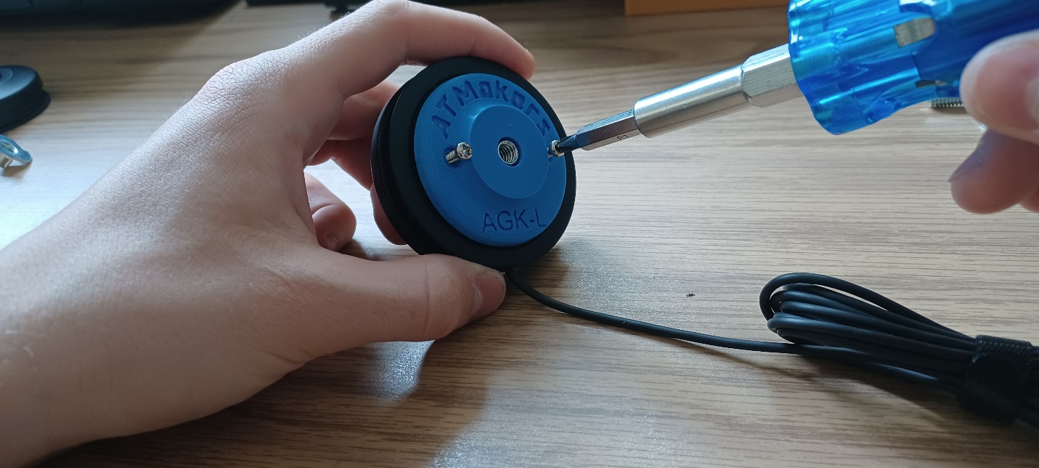
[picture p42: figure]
A screwdriver is used to tighten two screws in the adapter to attach the adapter to the Logitech Adaptive Gaming Button.

Now the device is complete!

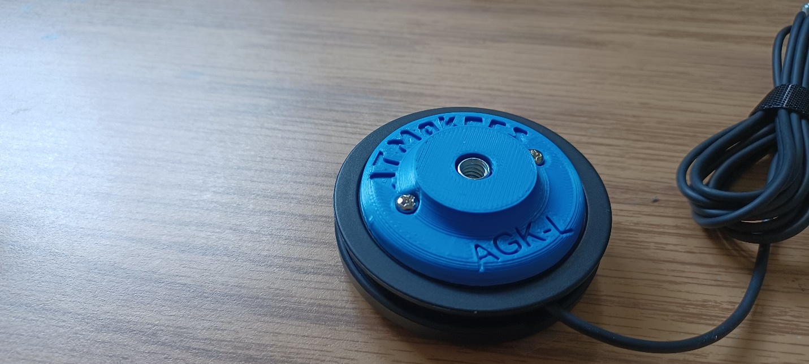
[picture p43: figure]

The Logitech Adaptive Gaming Kit button can now be mounted using to any device intended for cameras or camera equipment. Repeat as necessary for the other buttons in the kit.

© 2022 by Neil Squire / Makers Making Change This work is licensed under the CC BY SA 4.0 License: http://creativecommons.org/licenses/by-sa/4.0 Files available at https://makersmakingchange.com/camera-mount-adapters-for-the-logitech-adaptive-gaming-kit/ Page 1 of 1

V1.0 | June 2022 Camera Mount Adapters for the Logitech Adaptive Gaming Kit Assembly Guide

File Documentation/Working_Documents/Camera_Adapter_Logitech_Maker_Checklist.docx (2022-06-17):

# Maker To Do List

- Read through the Assembly Guide to become familiar with required hardware, tools, and mounting process.
- Talk to user and determine how many adapters are needed, and which of the four adapters are needed to customize their Logitech Adaptive Gaming Kit to their liking.
- Purchase hardware components.
- Referring to the 3D Print Guide, 3D Print the adapter.
- Insert T-nut into the into the adapter using the process in the Assembly Guide.
- Print User Guide.

# Items to Give to User

- Adapters with T-nut installed.
- M3 screws for attaching switch.
- User Guide.

© 2022 by Neil Squire / Makers Making Change This work is licensed under the CC BY SA 4.0 License: http://creativecommons.org/licenses/by-sa/4.0 Files available at https://makersmakingchange.com/camera-mount-adapters-for-the-logitech-adaptive-gaming-kit/ Page 1 of 1

V1.0 | June 2022 Camera Mount Adapters for the Logitech Adaptive Gaming Kit Maker Checklist

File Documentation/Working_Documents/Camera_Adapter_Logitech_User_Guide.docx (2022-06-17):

## Introduction

The Camera Mount Adapters for the Logitech Adaptive Gaming Kit provides a way to attach the various buttons from the Logitech Adaptive Gaming Kit to standard ¼”-20-inch camera mounting systems.

## Features

Threads to attach to Camera mount.

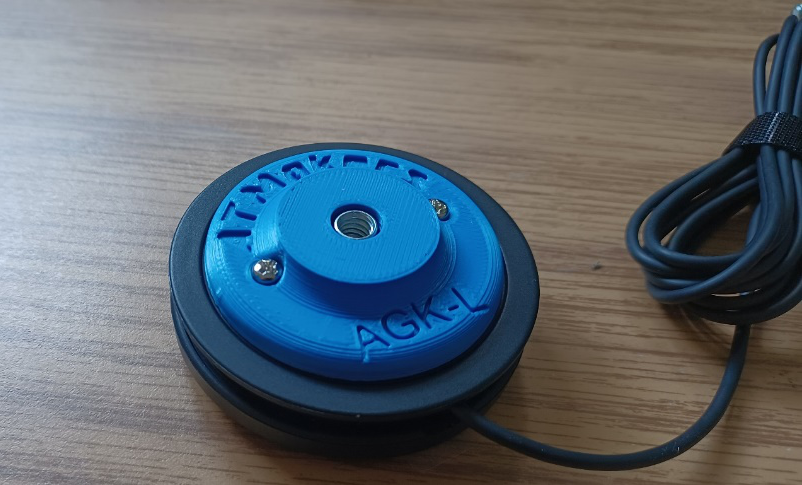
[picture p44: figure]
Camera Adapter for Logitech Switch Mount with arrows showing threads to attach to camera mount and screws to attach to Logitech button.

Screws to attach to Logitech button.

## Sizing

There are for different adapters to suit the different sizes of buttons from the Logitech adaptive gaming kit:

Size | Button | Camera Mount Adapter

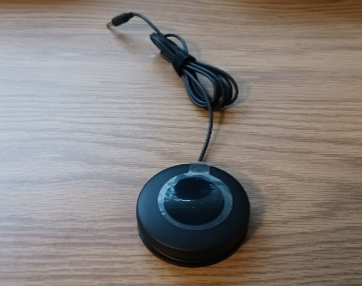
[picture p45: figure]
Logitech Large button on wood background.
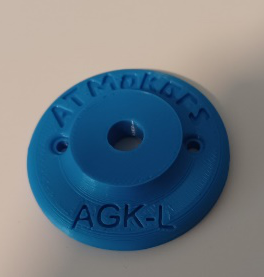
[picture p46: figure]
Camera mount adapter for Logitech Large Button on white background.

Large

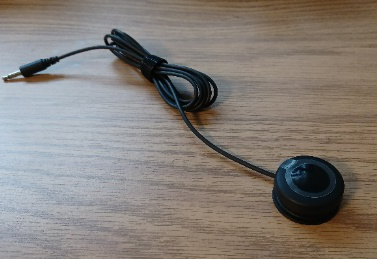
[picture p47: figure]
Logitech Small button on wood background.
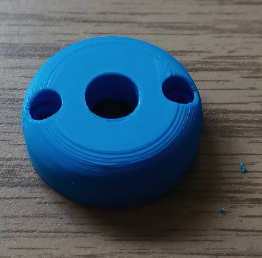
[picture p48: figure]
Camera mount adapter for Logitech Small Button on wood background.

Small

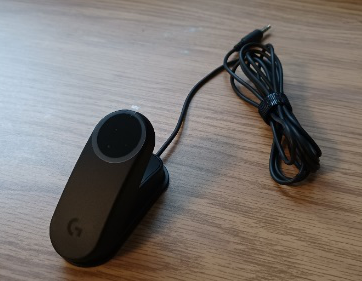
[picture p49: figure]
Logitech Trigger button on wood background.
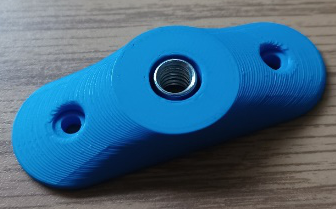
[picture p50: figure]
Camera mount adapter for Logitech Trigger Button on wood background.

Trigger

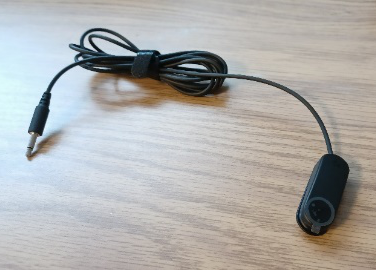
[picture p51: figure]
Logitech Light Touch button on wood background.
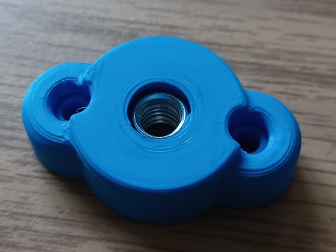
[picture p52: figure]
Camera mount adapter for Logitech Large Button on wood background.

Light Touch

### Installation

To attach the adapter to the Logitech Switches, place two M3 x 8 mm machine screws into the adapter. Line up the screw with the holes in the appropriate button and tighten the screws.

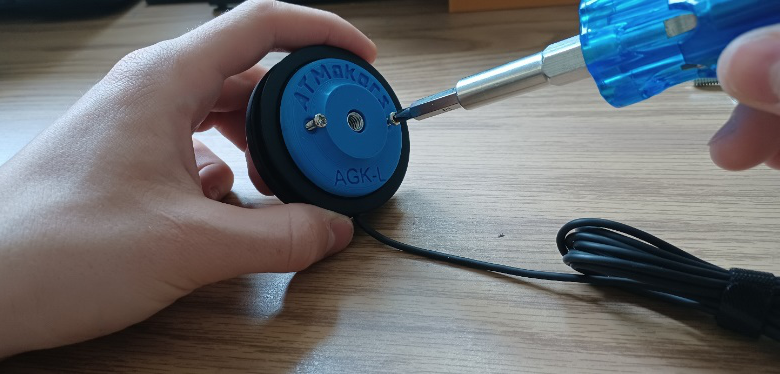
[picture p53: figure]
Camera Adapter for a Logitech Button being attached to the button with screws and a screwdriver.

To use with a camera mount, simply screw the camera mount threads into the adapter and adjust camera mount to the desired location.

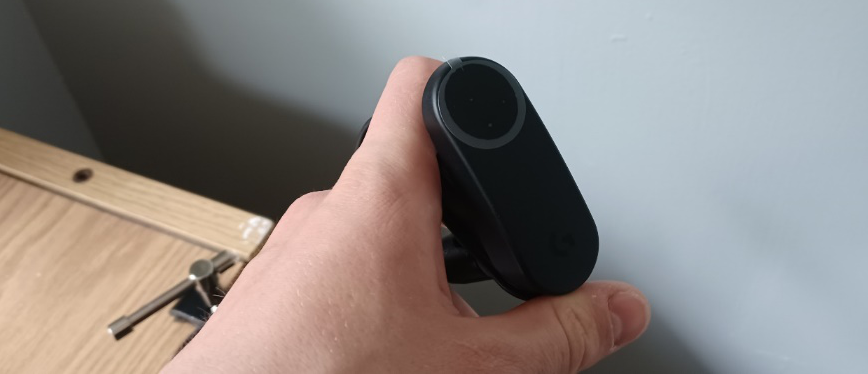
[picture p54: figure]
Logitech Trigger with Camera Mount Adapter being attached to Camera Mount.

## Cleaning

Wipe with sterilizing cloth or spray.

© 2022 by Neil Squire / Makers Making Change This work is licensed under the CC BY SA 4.0 License: http://creativecommons.org/licenses/by-sa/4.0 Files available at https://makersmakingchange.com/camera-mount-adapters-for-the-logitech-adaptive-gaming-kit/ Page 2 of 3

V1.0 | June 2022 Camera Adapters for the Logitech Adaptive Gaming Kit user Quick Guide

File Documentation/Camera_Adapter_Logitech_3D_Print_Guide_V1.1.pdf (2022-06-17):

V1.0 | June 2022

## Camera Mount Adapters for the Logitech Adaptive Gaming Kit

## 3D PRINTING GUIDE

© 2022 by Neil Squire / Makers Making Change This work is licensed under the CC BY SA 4.0 License: http://creativecommons.org/licenses/by-sa/4.0
Files available at https://makersmakingchange.com/camera-mount-adapters-for-the-logitech-adaptive-gaming-kit/ (https://makersmakingchange.com/project/camera-mount-adapter-for-logitech-large-button/) | Page 1 of 2

### 3D Printing Summary

Metrics | Entire Set
Total Print Time (min) | 9:54
Total Number of Components | 12
Typical Total Mass (g) | 10
Typical Number of Print Setups | 4

### 3D Printing Settings

Print File Name | Qt y | Individ ual Print Time (hr:min ) | Total Print Time (hr:min ) | Indivi dual Mass (g) | Total Mass (g) | Infill (%) | Suppor t | Layer Height/ Nozzle Diamete r(mm) | Notes (orientation, special settings, etc)
Large.stl | 3 | 1:13 | 3:39 | 11 | 33 | 20 | Suppor t Require d | 0.2/0.4 | -Needs Support Touching Build plate only - 2 perimeters minimum
Trigger.stl | 2 | 0:47 | 1:34 | 6 | 18 | 20 | Suppor t Require d | 0.2/0.4 | -Needs Support Touching Build plate only - 2 perimeters minimum
Small.stl | 3 | 0:35 | 1:45 | 4 | 12 | 20 | Suppor t Require d | 0.2/0.4 | -Needs Support Touching Build plate only - 2 perimeters minimum
Light_Touch.s tl | 4 | 0:44 | 2:56 | 5 | 20 | 20 | Suppor t Require d | 0.2/0.4 | -Needs Support Touching Build plate only - 2 perimeters minimum

### Customization Options

- Can be printed in any colour.

### Post-Processing

- Remove supports ensuring holes for barbs in T-nuts are uncovered.
- Follow Assembly guide for complete instructions on mounting the Logitech Large Button.

## Camera Mount Adapters for the Logitech Adaptive Gaming Kit

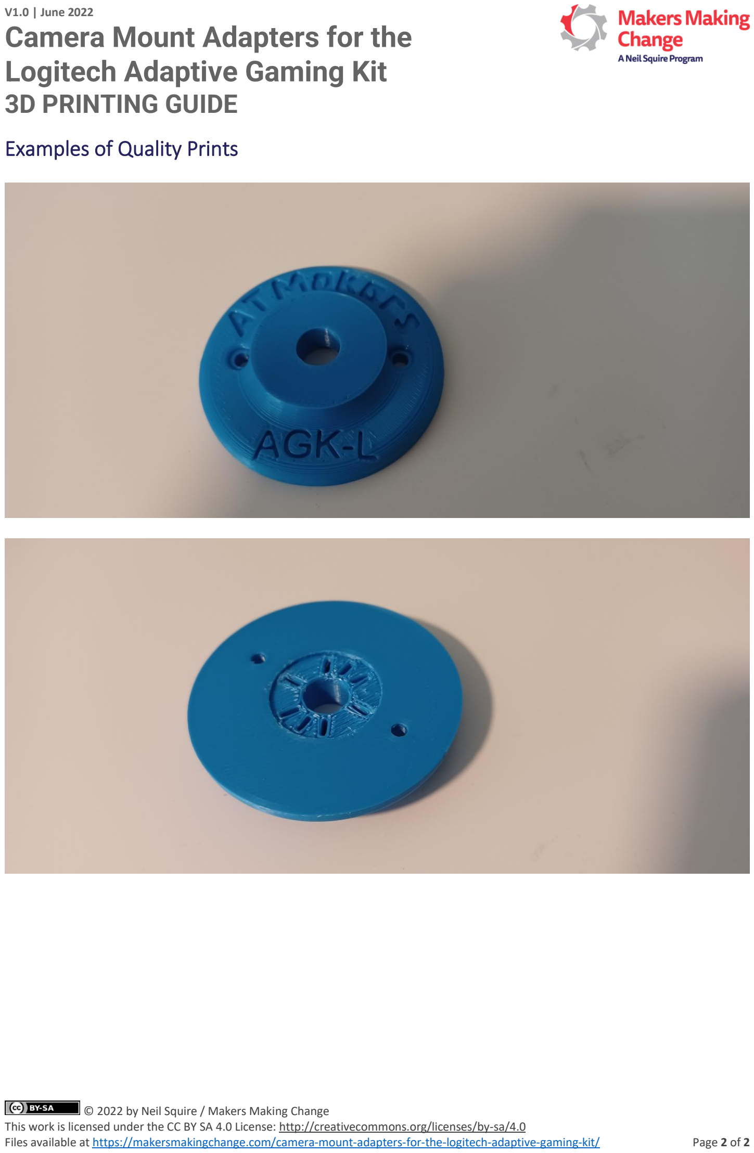
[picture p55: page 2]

V1.0 | June 2022

## 3D PRINTING GUIDE

© 2022 by Neil Squire / Makers Making Change This work is licensed under the CC BY SA 4.0 License: http://creativecommons.org/licenses/by-sa/4.0
Files available at https://makersmakingchange.com/camera-mount-adapters-for-the-logitech-adaptive-gaming-kit/ (https://makersmakingchange.com/project/camera-mount-adapter-for-logitech-large-button/) | Page 2 of 2

### Examples of Quality Prints

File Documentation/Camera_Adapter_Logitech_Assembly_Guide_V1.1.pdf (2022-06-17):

V1.0 | June 2022

# Camera Mount Adapters for the Logitech Adaptive Gaming Kit

# ASSEMBLY GUIDE

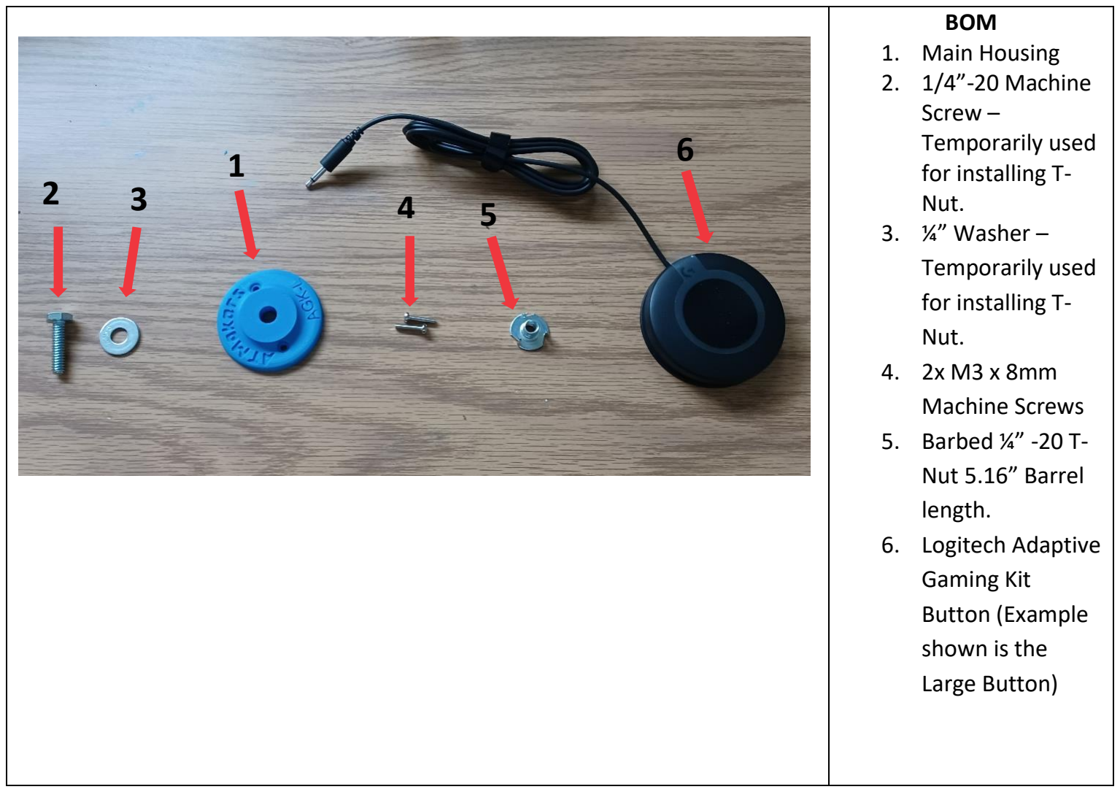
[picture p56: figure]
BOM 1. Main Housing 2. 1/4”-20 Machine Screw – Temporarily used for installing T- Nut. 3. ¼” Washer – Temporarily used for installing T- Nut. 4. 2x M3 x 8mm Machine Screws 5. Barbed ¼” -20 T- Nut 5.16” Barrel length. 6. Logitech Adaptive Gaming Kit Button (Example shown is the Large Button)

© 2022 by Neil Squire / Makers Making Change This work is licensed under the CC BY SA 4.0 License: http://creativecommons.org/licenses/by-sa/4.0
Files available at https://makersmakingchange.com/camera-mount-adapters-for-the-logitech-adaptive-gaming-kit/ (https://makersmakingchange.com/project/camera-mount-adapter-for-logitech-large-button/)

# Required Components

# Required Tools

- Screwdriver compatible with the M3 machine screws and the ¼” – 20 machine screw.

# Required Personal Protective Equipment (PPE)

## - None

# Logitech Adaptive Gaming Kit

# ASSEMBLY GUIDE

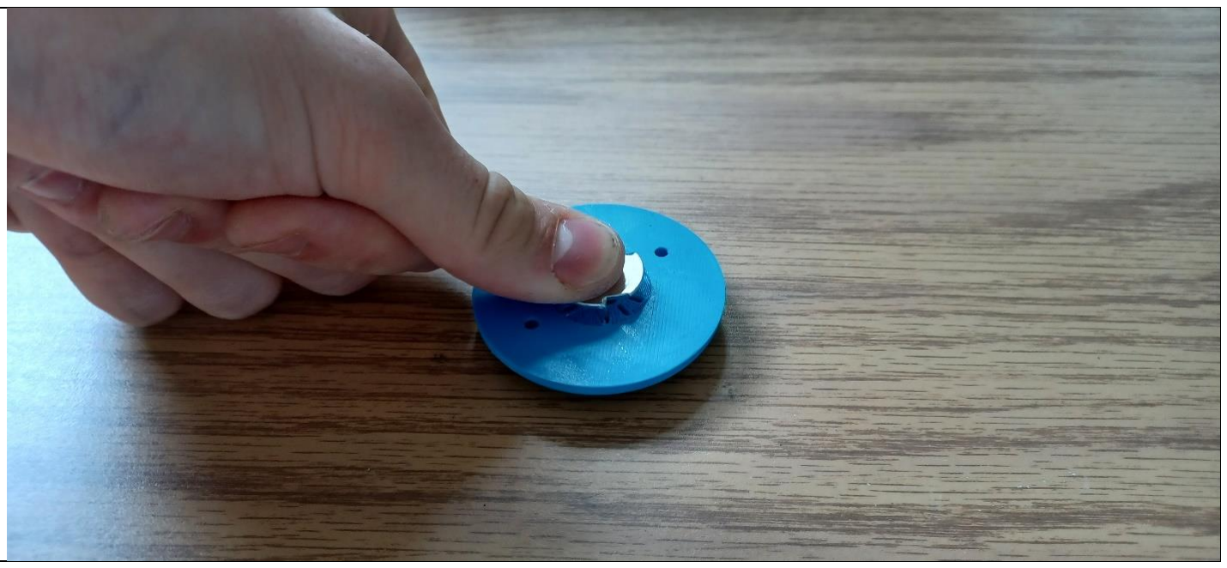
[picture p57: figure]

© 2022 by Neil Squire / Makers Making Change

# Assembly Instructions

## Step 1

Place the 3D-Printed Housing upside down on a table so that the text is facing downwards. Insert the T-Nut as far as possible into the hole by hand.

## Step 2

Flip the device so that the text is facing up and the T-Nut is sitting on the table. Put the ¼”

## washer on the ¼”-20 screw, then place the screw inside the hole from the top so that the

washer prevents it from falling through.

# Logitech Adaptive Gaming Kit

# ASSEMBLY GUIDE

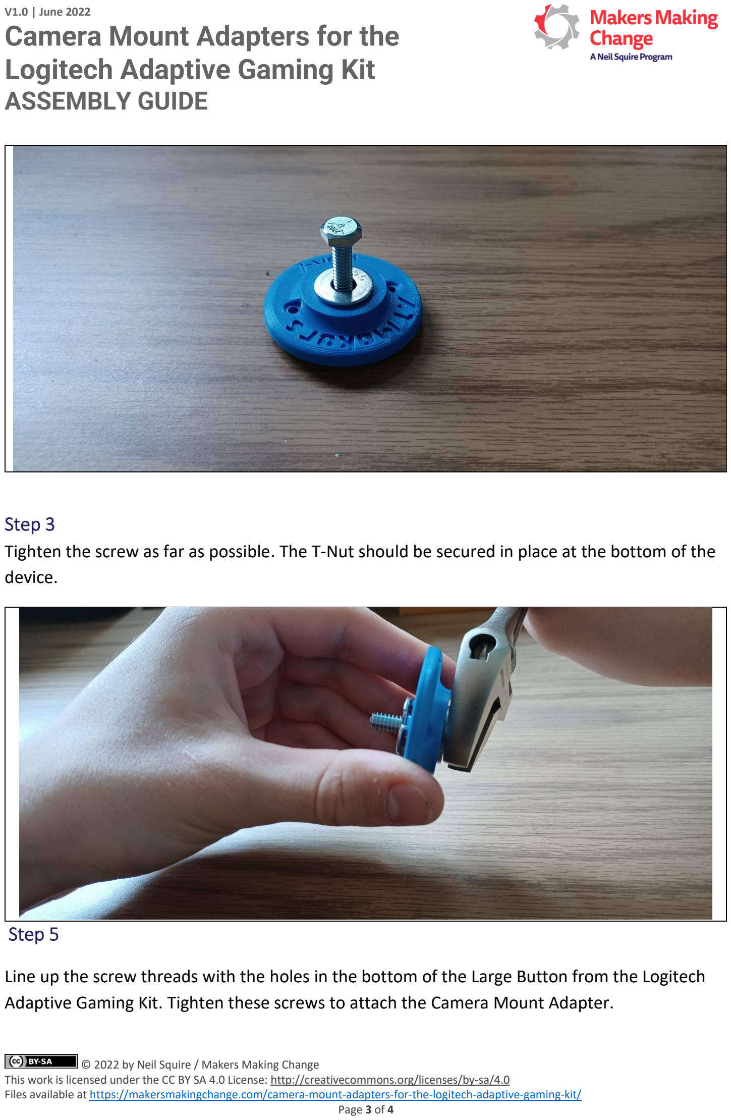
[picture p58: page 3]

© 2022 by Neil Squire / Makers Making Change

## Step 3

Tighten the screw as far as possible. The T-Nut should be secured in place at the bottom of the device.

## Step 5

Line up the screw threads with the holes in the bottom of the Large Button from the Logitech Adaptive Gaming Kit. Tighten these screws to attach the Camera Mount Adapter.

# Logitech Adaptive Gaming Kit

# ASSEMBLY GUIDE

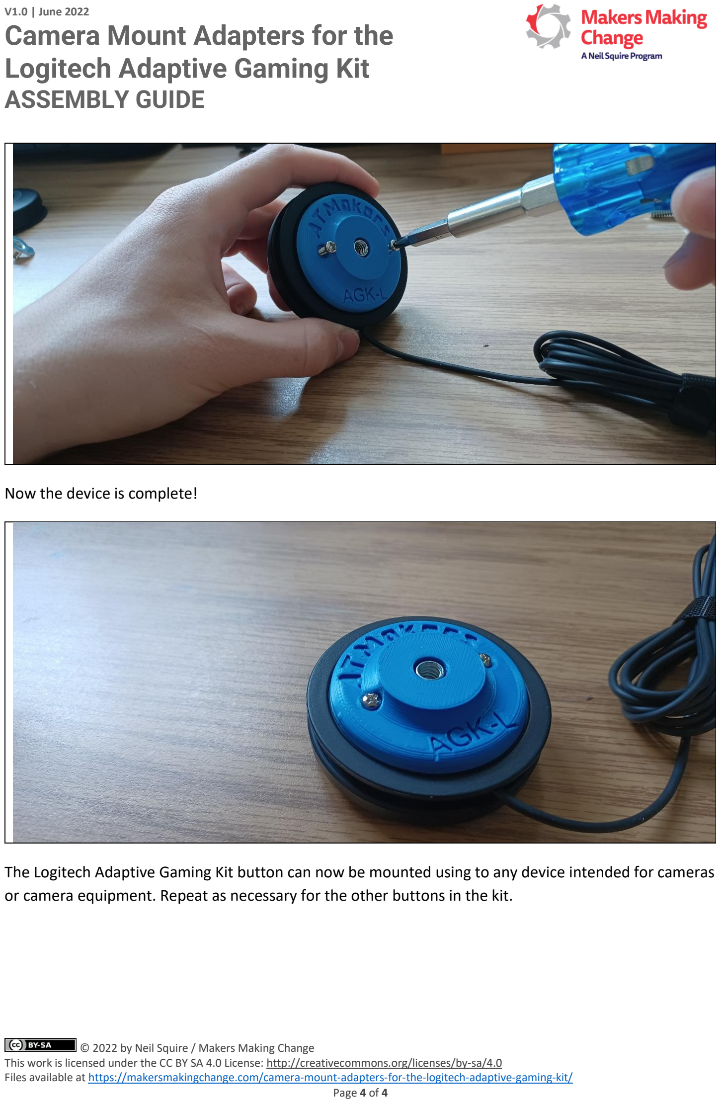
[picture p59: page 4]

© 2022 by Neil Squire / Makers Making Change

## Now the device is complete!

The Logitech Adaptive Gaming Kit button can now be mounted using to any device intended for cameras or camera equipment. Repeat as necessary for the other buttons in the kit.

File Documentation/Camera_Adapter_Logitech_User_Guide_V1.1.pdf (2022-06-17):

V1.0 | June 2022

# Camera Adapters for the Logitech Adaptive Gaming Kit

## USER QUICK GUIDE

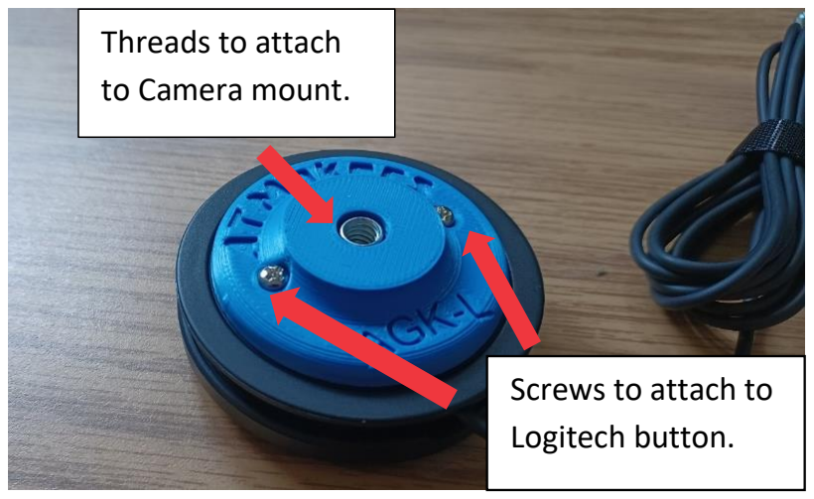
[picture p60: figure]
Screws to attach to Logitech button.; Threads to attach to Camera mount.
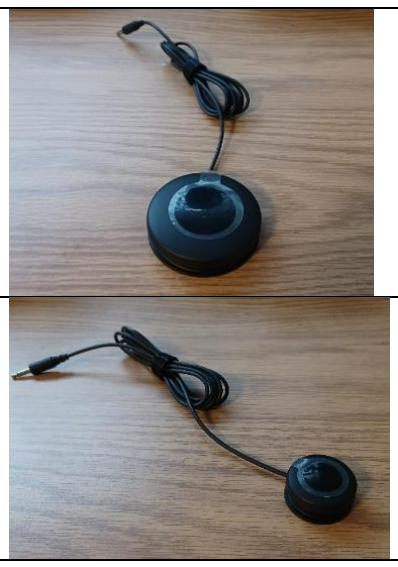
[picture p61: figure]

© 2022 by Neil Squire / Makers Making Change

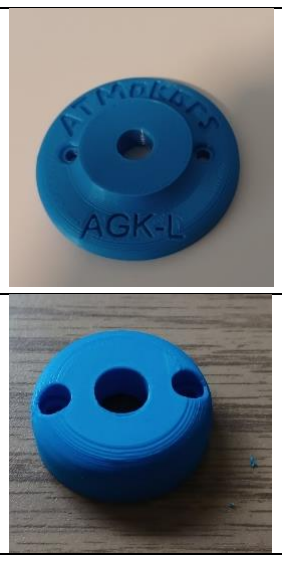
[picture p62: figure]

This work is licensed under the CC BY SA 4.0 License: http://creativecommons.org/licenses/by-sa/4.0
Files available at https://makersmakingchange.com/camera-mount-adapters-for-the-logitech-adaptive-gaming-kit/ (https://makersmakingchange.com/project/camera-mount-adapter-for-logitech-large-button/)

### Introduction

The Camera Mount Adapters for the Logitech Adaptive Gaming Kit provides a way to attach the various buttons from the Logitech Adaptive Gaming Kit to standard ¼”-20-inch camera mounting systems.

### Features

### Sizing

There are for different adapters to suit the different sizes of buttons from the Logitech adaptive gaming kit:

Size | Button | Camera Mount Adapter
Large

Small

V1.0 | June 2022

# Camera Adapters for the Logitech Adaptive Gaming Kit

## USER QUICK GUIDE

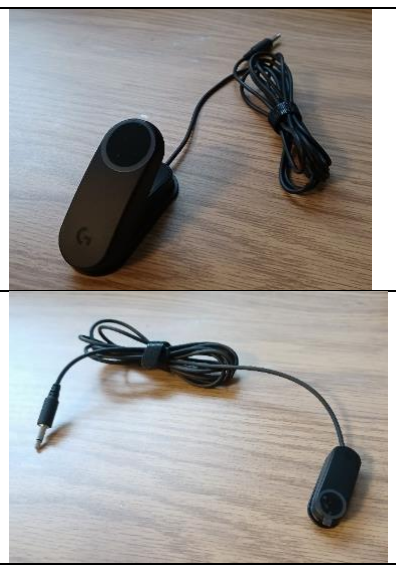
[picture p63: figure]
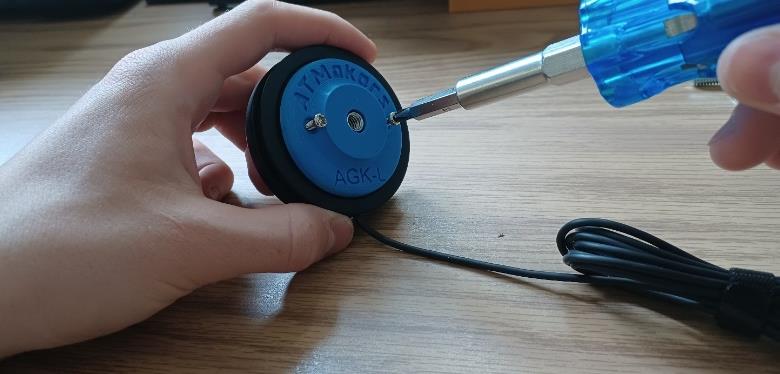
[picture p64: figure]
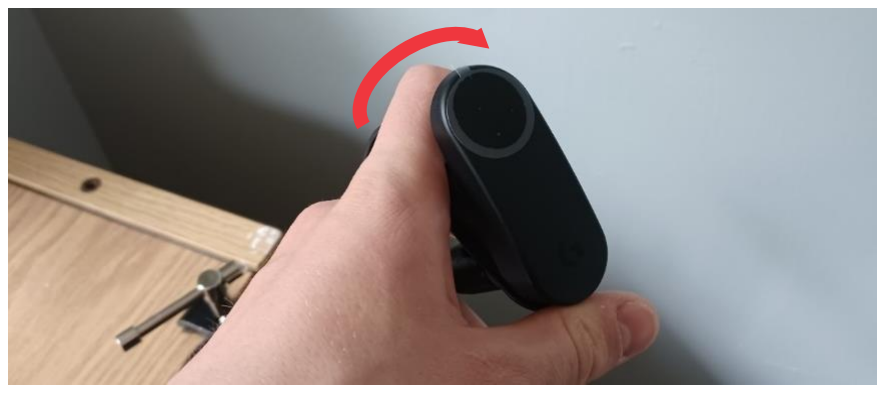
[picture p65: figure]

© 2022 by Neil Squire / Makers Making Change

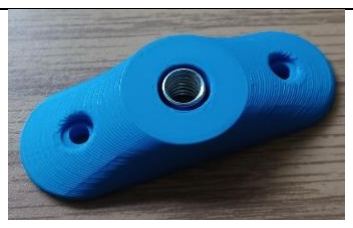
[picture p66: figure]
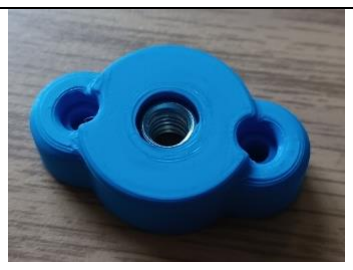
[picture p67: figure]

This work is licensed under the CC BY SA 4.0 License: http://creativecommons.org/licenses/by-sa/4.0
Files available at https://makersmakingchange.com/camera-mount-adapters-for-the-logitech-adaptive-gaming-kit/ (https://makersmakingchange.com/project/camera-mount-adapter-for-logitech-large-button/)

Trigger

Light Touch

Installation
To attach the adapter to the Logitech Switches, place two M3 x 8 mm machine screws into the adapter. Line up the screw with the holes in the appropriate button and tighten the screws.

To use with a camera mount, simply screw the camera mount threads into the adapter and adjust camera mount to the desired location.

### Cleaning

Wipe with sterilizing cloth or spray.

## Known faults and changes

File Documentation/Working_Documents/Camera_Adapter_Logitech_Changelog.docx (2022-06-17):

# Version 1.1 | Date 05/26/2022

- Documentation created by Neil Squire / Makers Making Change.

Minor Modifications by Neil Squire:

- Changed the length of the hole for the screws so that all buttons can be attached with the same length of screw.
- The width of the countersink of the screw holes were made larger to accommodate screws with wider heads.
- All the depths of the T-Nut inserts were different, some too deep or too shallow, so all were changed to 2.4mm. (T-Nut flush with bottom with some margin)
- All the heights of the mounts were different, and all heights were changed to approx. 9.5mm. (T-Nut flush with top of mount).

# Version 1.0 | Date 01/26/2020

Design created by AT Makers

© 2022 by Neil Squire / Makers Making Change This work is licensed under the CC BY SA 4.0 License: http://creativecommons.org/licenses/by-sa/4.0 Files available at https://makersmakingchange.com/camera-mount-adapters-for-the-logitech-adaptive-gaming-kit/ Page 1 of 1

V1.0 | June 2022 Camera Mount Adapters for the Logitech Adaptive Gaming Kit changelog
